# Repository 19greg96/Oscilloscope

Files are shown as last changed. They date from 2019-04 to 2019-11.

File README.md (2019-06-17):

# Oscilloscope
Simple two channel oscilloscope, function generator and bode plotter for STM32 NUCLEO-F446RE board.

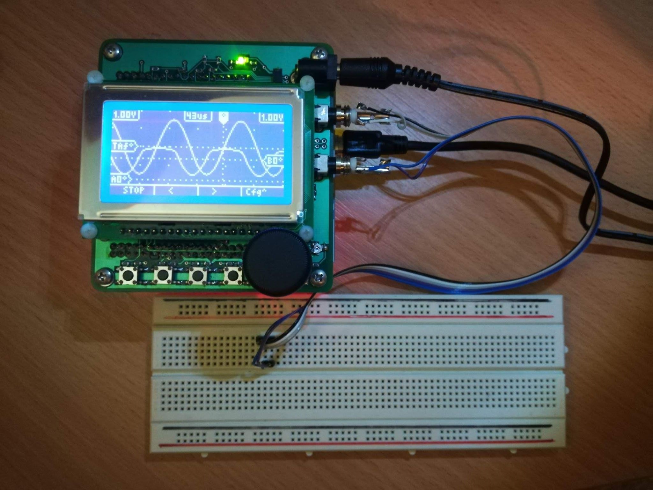
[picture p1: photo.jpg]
Picture of oscilloscope measuring effect of LED on DAC channel 2, when internal DAC buffer is disabled

Picture of oscilloscope measuring effect of LED on DAC channel 2, when internal DAC buffer is disabled.

## Issues with the hardware design:
 - Input voltage range is bad (5Vpp). This can be extended by switchable voltage divider on input.
 - No separate analog / digital ground plane.
 - Input trace has no extra clearance from ground planes.
 - GPIO pin allocation is not optimised for header side, leading to many cross board signal connections.
 - No control of anti-alias filter cut-off frequency.
 - No hardware gain control (op-amp reference should be at Vcc/2).
 - In DC coupling mode, there is a Vcc/2 offset caused by the bias for AC coupling.
 - There is an offset voltage on channel A for some reason (this could be fixed in software, but hardware explanation would be better).
 - AC coupling cutoff frequency could be lower.
 - AC coupling cutoff frequency is changed by external resistance, because there is no buffer directly on the input. (buffer needs a negative voltage rail for this)
 - DAC output single resistor is not enough for power rating. Minimum two parallel resistors are needed for 3.3V max output.
 - Max DAC output voltage is little less than Vref.
 - No support of negative DAC output.
 - Rotary encoder is too close to buttons and GLCD.
 - DC and IO jacks do not hang far enough off of PCB edge to enable boxing of device.
 - GLCD is upside-down making contrast bad at normal viewing angles.
 - No support fot 4W measurement.

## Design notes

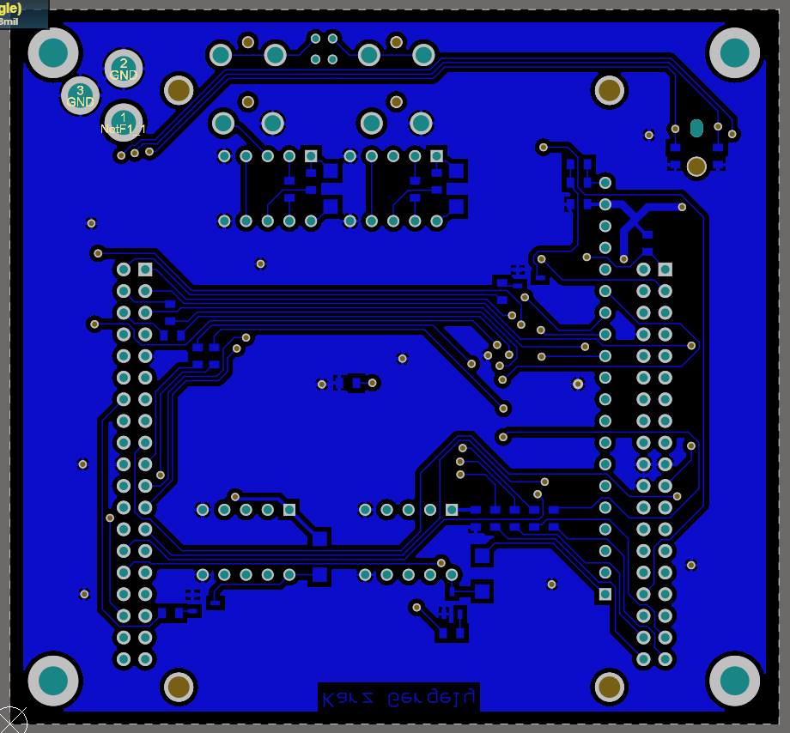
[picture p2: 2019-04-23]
oscilloscope/oscilloscope/Project Outputs for Oscilloscope/BOT_no_silk.PNG

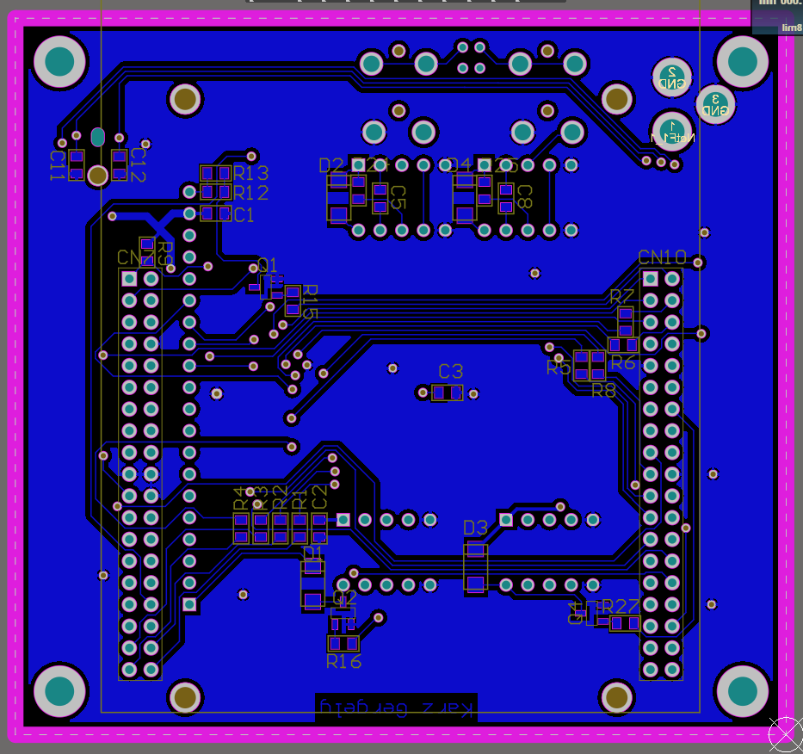
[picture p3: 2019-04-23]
oscilloscope/oscilloscope/Project Outputs for Oscilloscope/BOT_mirrored.png

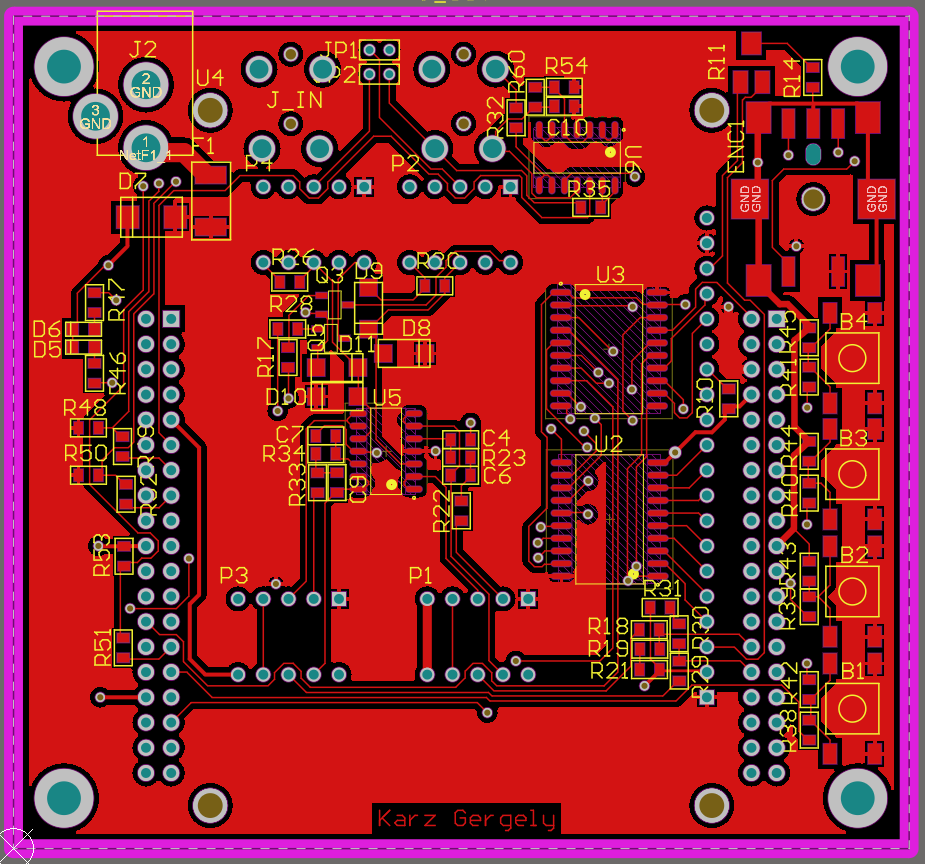
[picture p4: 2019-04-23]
oscilloscope/oscilloscope/Project Outputs for Oscilloscope/TOP.PNG

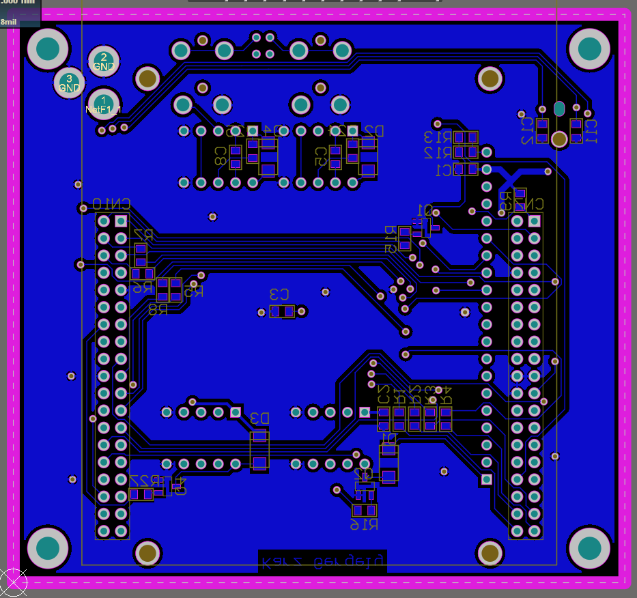
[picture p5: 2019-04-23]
oscilloscope/oscilloscope/Project Outputs for Oscilloscope/BOT.PNG

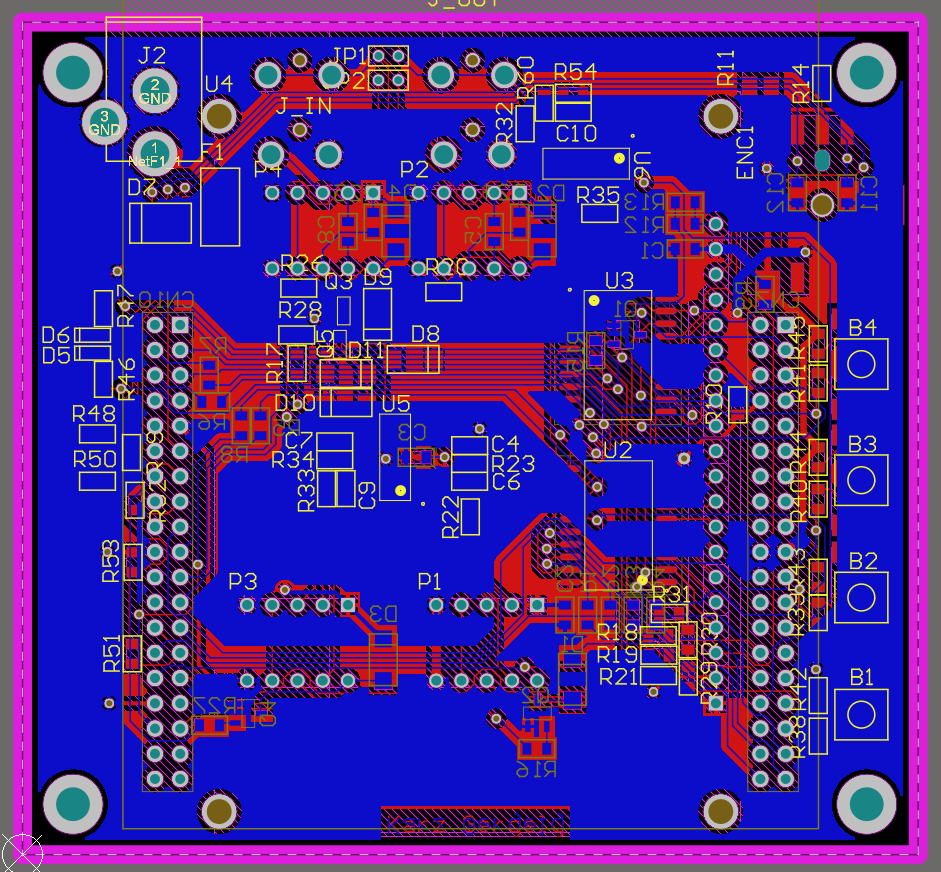
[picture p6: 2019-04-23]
oscilloscope/oscilloscope/Project Outputs for Oscilloscope/Capture.PNG

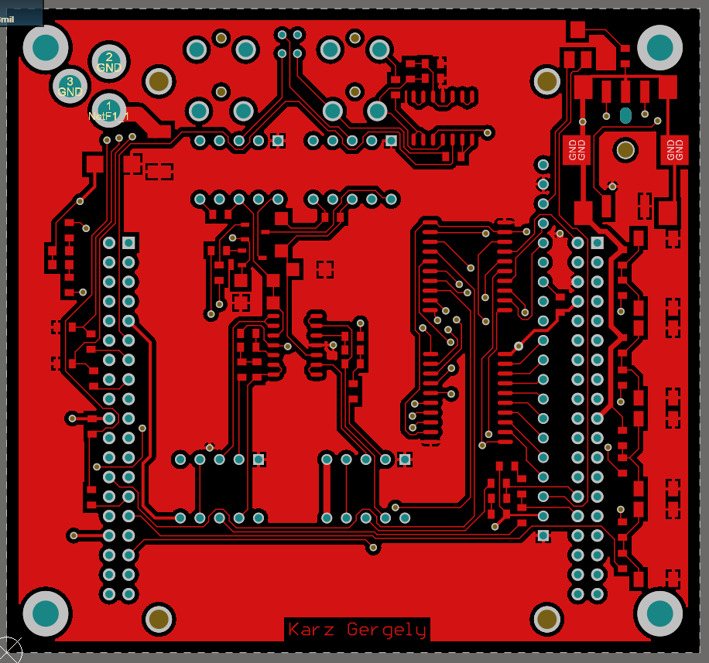
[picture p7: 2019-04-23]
oscilloscope/oscilloscope/Project Outputs for Oscilloscope/TOP_no_silk.PNG

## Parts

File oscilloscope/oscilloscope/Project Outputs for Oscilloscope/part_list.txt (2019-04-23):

Comment	Reference	Description	Designator	Footprint	LibRef	Quantity

"Button"	"45-05-42"	"Push button"	"B1, B2, B3, B4"	"FP_BTN_SMD"	"Button"	"4"
"100nF"	"82-10-76"	"Capacitor"	"C1, C2, C3, C10"	"FP_0805_CAP_085"	"CAP 100nF"	"4"
"10nF"	"82-11-02"	"Capacitor"	"C4, C5, C6, C7, C8, C9, C11, C12"	"FP_0805_CAP_085"	"CAP 10nF"	"8"
"SCHOTTKY SMA"	"83-02-20"	"Schottky diode"	"D1, D2, D3, D4, D8, D9, D10, D11"	"FP_SMA"	"SCHOTTKY SMA"	"8"
"LED Green"	"95-01-09"	"Green LED"	"D5"	"FP_0805_LED_RED"	"LED Green"	"1"
"LED Red"	"95-01-68"	"Red LED"	"D6"	"FP_0805_LED_RED"	"LED Red"	"1"
"TRANS SUPPR"	"96-03-67"	"Transient suppressor"	"D7"	"FP_SMB"	"TRANS SUPPR"	"1"
"Rotary Encoder"	""	"Encoders 9.5 MM SHAFT W/SWITCH 2 DET"	"ENC1"	"FP_PEC11S"	"PEC11S-929K"	"1"
"Multifuse"	"44-04-71"	"1812 Multifuse"	"F1"	"FP_MULTIFUSE"	"Multifuse"	"1"
"2.xmm"	"43-07-67"	"2.xmm DC HEBA25 TÁPFESZÜLTSÉG ALJZAT ZÁRT, NYÁKBA 90°"	"J2"	"FP_DC_TAP_ANYA"	"DC_TAP_ANYA"	"1"
"35mm Audio Jack 3 contact"	"1267376"	"3.5mm Audio Jack MX-387GL"	"J_IN, J_OUT"	"FP_35MM_JACK_SMALL_3PIN"	"35mm Audio Jack 3 contact"	"2"
"JUMPER"	""	"Jumper Wire"	"JP1, JP2"	"FP_CONN2_TUSKE_2MM_1.5+3.2"	"JUMPER"	"2"
"Relay"	"42-17-08"	"Mini DPDT relay 14x9x5mm"	"P1, P2, P3, P4"	"FP_RELAY"	"Relay Mini DPDT"	"4"
"2N7002"	"86-05-52"	"N-channel MOSFET"	"Q1, Q2, Q3, Q4, Q5"	"FP_SOT23-3"	"2N7002"	"5"
"1K"	"81-27-93"	"Resistor"	"R1, R2, R3, R4, R5, R6, R7, R8, R18, R19, R21, R29, R30, R31, R38, R39, R40, R41, R51"	"FP_0805_RES"	"RES 1K"	"19"
"100K"	"81-30-68"	"Resistor"	"R9"	"FP_0805_RES"	"RES 100K"	"1"
"10K"	"81-30-45"	"Resistor"	"R10, R15, R16, R17, R27, R28, R42, R43, R44, R45, R48, R49, R50, R52, R53, R54, R60"	"FP_0805_RES"	"RES 10K"	"17"
"4K7"	"90-00-68"	"4K70 3305-472R (KIC) 3x3.8mm CERMET"	"R11"	"FP_CERMET_SMD"	"Cermet Pot 4K7"	"1"
"100R"	"81-30-00"	"Resistor"	"R12, R13"	"FP_0805_RES"	"RES 100R"	"2"
"6K8"	"81-30-41"	"Resistor"	"R14"	"FP_0805_RES"	"RES 6K8"	"1"
"2M00"	"80-17-98"	"Resistor"	"R20, R24, R25, R26"	"FP_0805_RES"	"RES 2M"	"4"
"820R"	"81-30-21"	"Resistor"	"R22, R23, R33, R34"	"FP_0805_RES"	"RES 820R"	"4"
"150R"	"81-10-77"	"Resistor"	"R32, R35, R46, R47"	"FP_0805_RES"	"RES 150R"	"4"
"NUCLEO-F446RE"	"NUCLEO"	""	"U1"	"FP_NUCLEO-64"	"NUCLEO-F446RE"	"1"
"74HCT245"	"87-06-35"	"8x Bidirectional bus transciever"	"U2"	"FP_SOP127P1030X265-20M"	"74HCT245"	"1"
"74HCT244D"	"87-05-95"	"8xBuffer/Line Driver"	"U3"	"FP_SOP127P1030X265-20M"	"74HCT244D"	"1"
"GLCD_64128Q"	"37-00-71"	"64128QCCBW-3LP"	"U4"	"FP_GLCD_64128Q"	"GLCD_64128Q"	"1"
"MCP6004T-I/SL"	"1627186"	"Operational Amplifier, Quad, 4 Amplifier, 1 MHz, 0.6 V/µs, 1.8V to 5.5V, SOIC, 14 Pins"	"U5, U6"	"FP_SOIC127P600X175-14M"	"MCP6004T-I/SL"	"2"

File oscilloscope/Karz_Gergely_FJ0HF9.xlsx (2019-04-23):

Item # | Supplier | Reference | Name | Quantity
1 | Farnell | 1267376 | MX-387GL - Phone Audio Connector, 3 Contacts, Jack, 3.5 mm, PCB Mount, Metal Body | 2
2 | Farnell | 1627186 | MCP6004T-I/SL - Operational Amplifier | 2
3 | Lomex | 43-07-67 | TÁP DC ANYA 5.5/2.1/9.5mm DCS-5521-5 | 1
4 | Lomex | 90-00-68 | 4K70 3305-472R (KIC) 3x3.8mm CERMET | 1
5 | Lomex | 87-06-35 | 74HCT245D Transceiver, 74HCT245 | 1
6 | Lomex | 87-05-95 | 74HCT244D-Q100,118 Buffer / Line Driver, 74HCT244 | 1
7 | Lomex | 44-04-71 | 1.25A 15V 1812L125/16DR POLYFUSE SMD 1812 (LFS) ˝LF125-16˝ | 1
8 | Lomex | 37-00-71 | 128x 64 DOT LIGHT:LED 64128QCCBW-3LP (DIS) 0.4/DOT 75x53mm BLUE STN LOW.POW. WIDE TEMP. (CONTROLLER/DRIVER: SBN6400G-D + SBN0064G-D) | 1
9 | Lomex | 82-10-76 | 100nF 0805 10% 50V X7R 0805B104K500CT (WAL) | 4
10 | Lomex | 82-11-02 | 10nF 0805 10% 100V X7R 08051C103KAT2A (AVX) | 8
11 | Lomex | 95-01-09 | 2012 GREEN 568nm 15mcd KP-2012SGC (KIN) W.CLEAR 2x1.2x1.1mm 0805 120° | 1
12 | Lomex | 42-17-08 | MECH 5V 2xMORSE 1A/30VDC 0.5A/12VAC A5W-K (TAK) 178R 14x9x5mm | 4
13 | Lomex | 86-05-52 | MOSFET Transistor, N Channel, 300mA, 60V, 2.8 ohm, 10V, 2V | 5
14 | Lomex | 45-05-42 | TACT 6x 6 4P SPST 1 FSM2JSMA (TYC) 50mA 12VDC SMD H=4.3mm 160g BLACK B. 2-1437565-7 | 4
15 | Lomex | 95-01-68 | 2012 RED 640nm 100mcd KP-2012SRC-PRV (KIN) W.CLEAR 2x1.2x1.1mm 0805 120° | 1
16 | Lomex | 81-27-93 | 1K00 0805 5% WR08X102JTL 0.125W (WAL) | 19
17 | Lomex | 81-30-68 | 100K 0805 5% WR08X104JTL 0.125W (WAL) | 1
18 | Lomex | 81-30-45 | 10K0 0805 5% CR-05JL7---10K 0.125W (VIK) | 17
19 | Lomex | 81-30-00 | 100R 0805 5% WR08X101JTL 0.125W (WAL) | 2
20 | Lomex | 81-30-41 | 6K80 0805 5% WR08X682JTL 0.125W (WAL) | 1
21 | Lomex | 80-17-98 | 2M00 0805 1% CR-05FL7---2M0 0.125W (VIK) | 4
22 | Lomex | 81-30-21 | 820R 0805 5% WR08X821JTL 0.125W (WAL) | 4
23 | Lomex | 81-10-77 | 150R 0805 5% CR-05JL7--150R 0.125W (VIK) | 4
24 | Lomex | 83-02-20 | 1A 40V DO-214AC SCH.RECT.LOW Vf SSL14 (TSC) SMA | 8
25 | Lomex | 96-03-67 | 6.7V Ubr 600W UNIDIR. 5V Urwm SMBJ5.0A (STM) DO-214AA (SMB) ˝BUZ˝ | 1
26 | Tanszék | NUCLEO | Nucleo F446RE | 1
27 | Lomex | 24-01-70 | ADAPTER 2000mA 5VDC KAPCSOLÓ ÜZEM 5V 2A SA110R-05GS-I (SAC) TÜV/CE 5.5/2.1mm DUGÓ EFF.LEVEL VI STANDBY POWER <0,075W | 1
28 | Lomex | 43-08-37 | TÜSKESOR 40 P PHSS-40-12/3 (T-T) 2.54mm PIN 0.64x0.64 TÖRDELHETÖ | 1
29 | Lomex | 43-00-08 | HÜVELY 20 P FHSH-2.54-20 (T-T) 1# h=8,5mm AU. | 1
30 | Lomex | 43-07-86 | JUMPER 2 P ANYA MJF-6MM (T-T) 1# FEKETE FÜLES | 2
31 | Lomex | 43-18-67 | JACK 3.5mm APA JM35STPATB (T-T) SZTEREO A-V | 2
32 | Lomex | 43-08-40 | BNC 1 P ANYA BNC-S12 (FEM) H-F SORKAPOCS BEKÖTÉSŰ LENGŐ | 4
33 | Lomex | 54-00-25 | ARNY.KÁBEL 2x0.08 AK-2-0.08F ( ) BLACK 2xD=2.8mm FLAT | 1

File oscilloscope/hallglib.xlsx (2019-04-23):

Item # | Column=Supplier | Column=Reference | Column=Name | Column=Quantity
1
2
3

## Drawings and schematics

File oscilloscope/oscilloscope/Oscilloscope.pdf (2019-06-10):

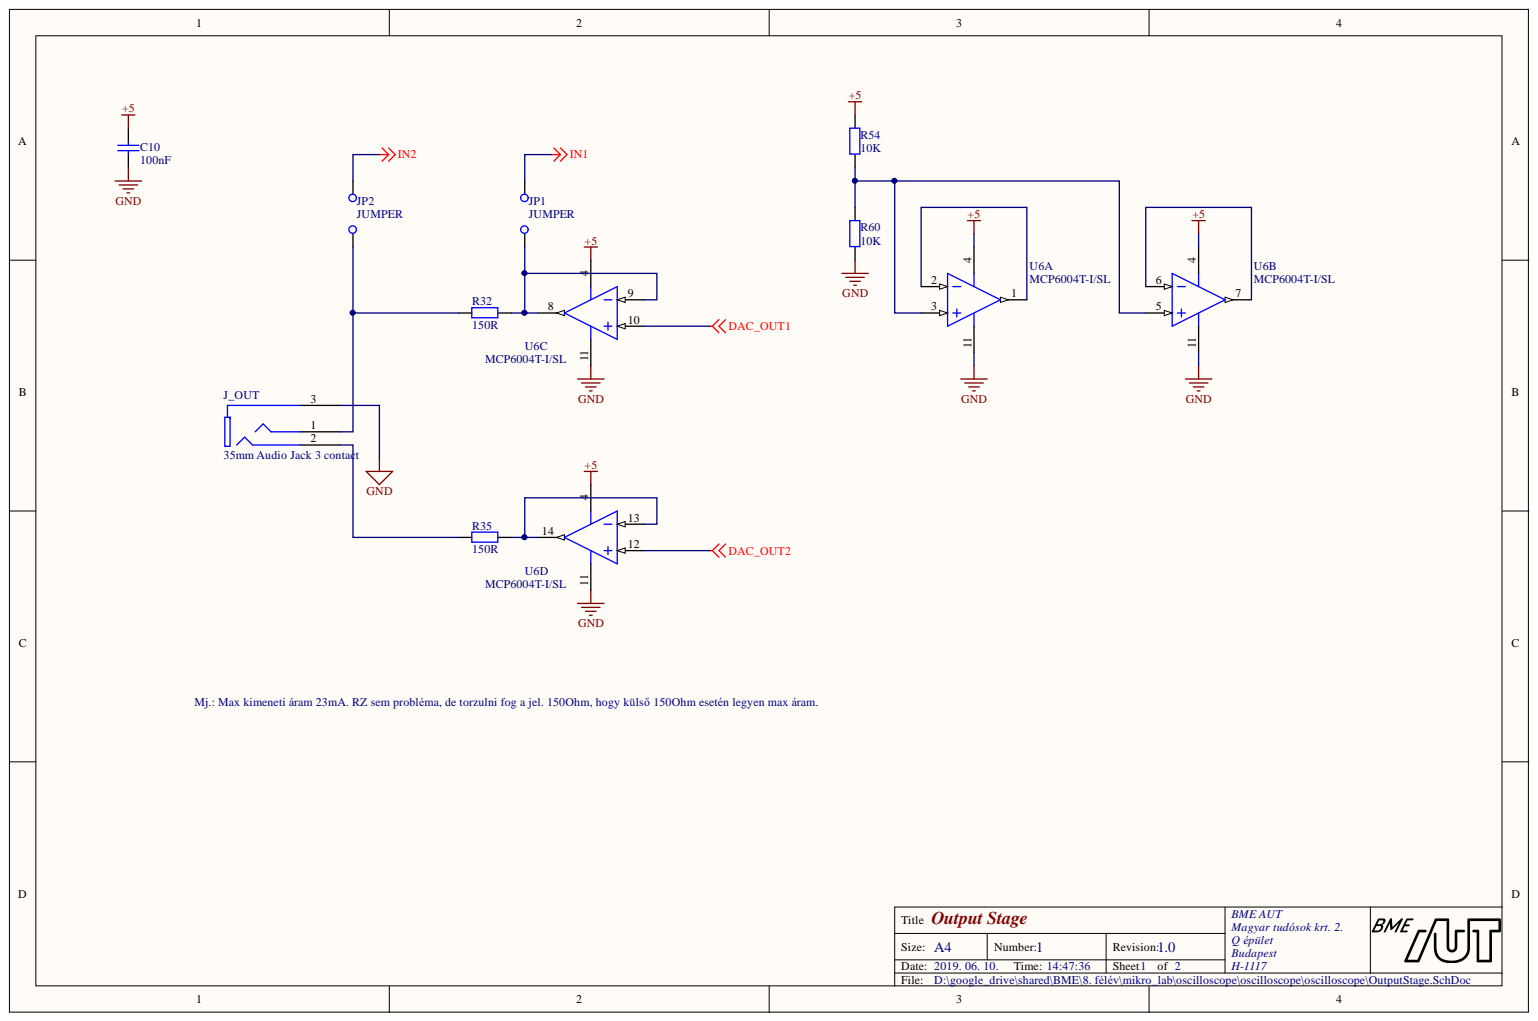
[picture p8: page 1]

Mj.: Max kimeneti áram 23mA. RZ sem probléma, de torzulni fog a jel. 150Ohm, hogy külső 150Ohm esetén legyen max áram.

Output Stage Title | BME AUT Magyar tudósok krt. 2. Q épület Budapest H-1117

A4 Size: | 1 Number: | 1.0 Revision:
Date: 2019. 06. 10. Time: 14:47:36 | | Sheet of 2

D:\google_drive\shared\BME\8. félév\mikro_lab\oscilloscope\oscilloscope\oscilloscope\OutputStage.SchDoc

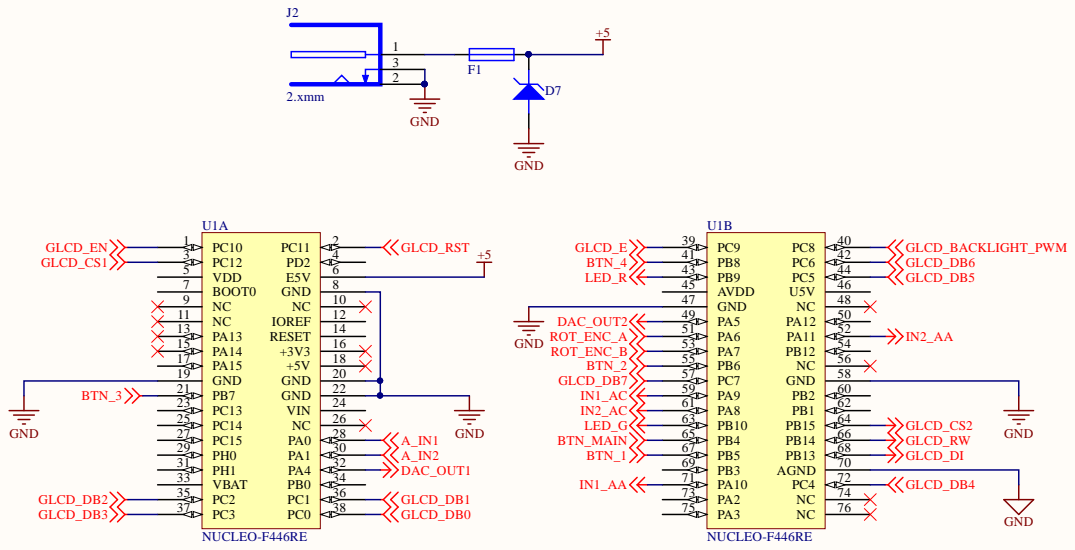
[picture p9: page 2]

Nucleo Title | BME AUT Magyar tudósok krt. 2. Q épület Budapest

A4 Size: | 1 Number: | 1.0 Revision:

D:\google_drive\shared\BME\8. félév\mikro_lab\oscilloscope\oscilloscope\oscilloscope\Nucleo.SchDoc

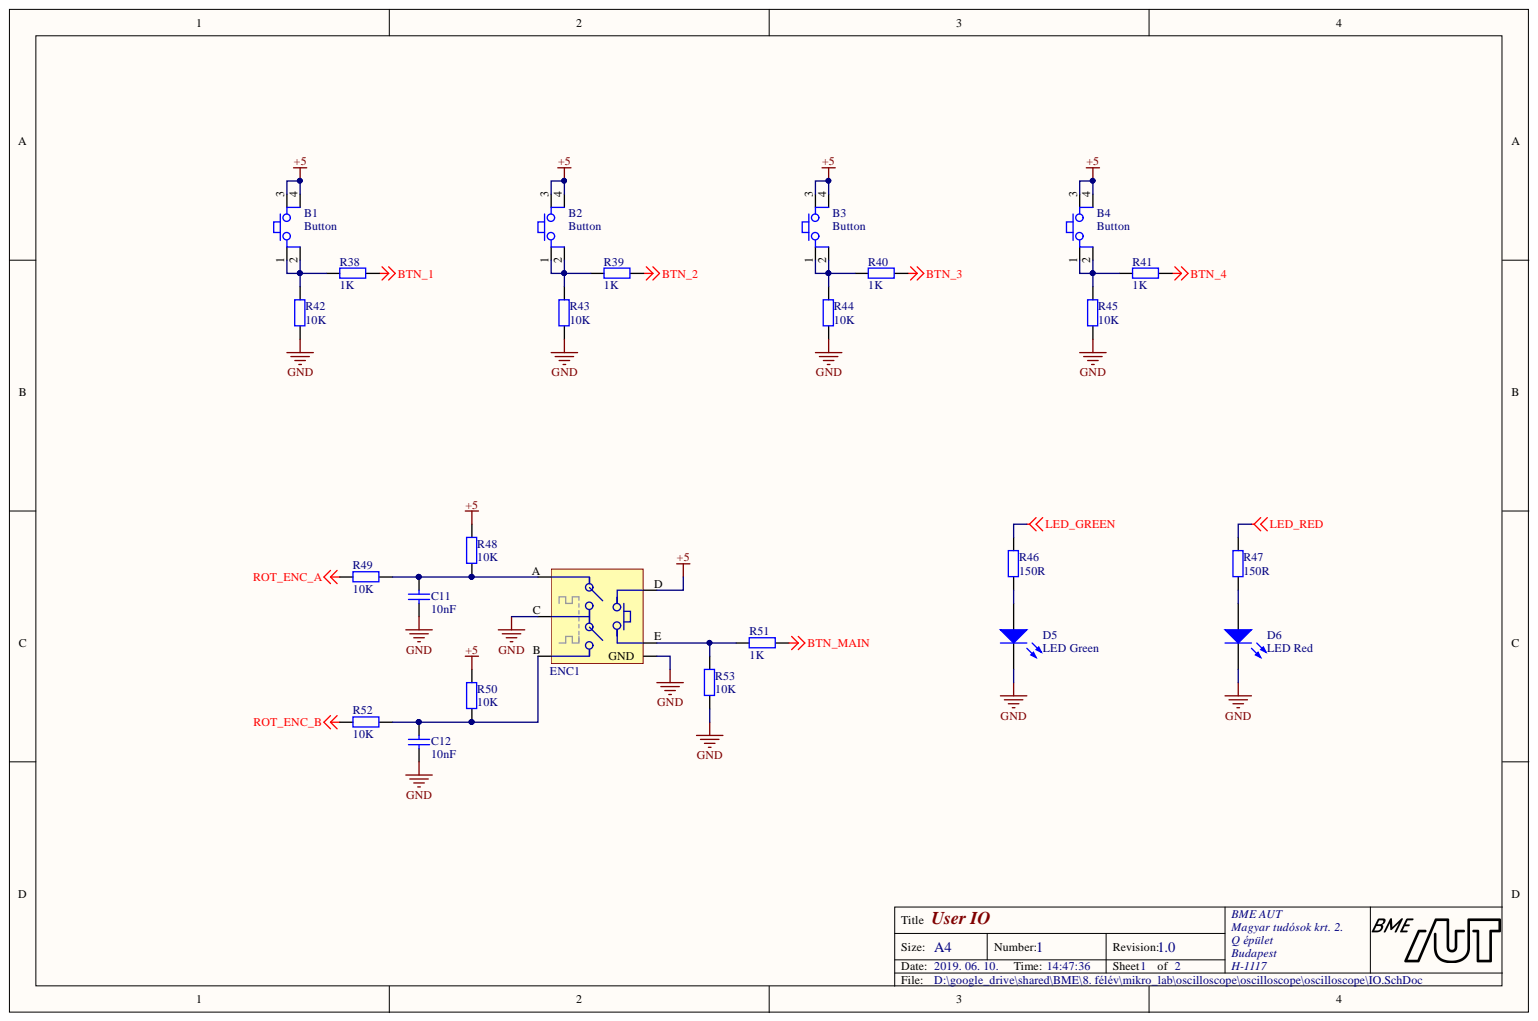
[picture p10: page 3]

User IO Title | BME AUT Magyar tudósok krt. 2. Q épület Budapest

A4 Size: | 1 Number: | 1.0 Revision:

D:\google_drive\shared\BME\8. félév\mikro_lab\oscilloscope\oscilloscope\oscilloscope\IO.SchDoc

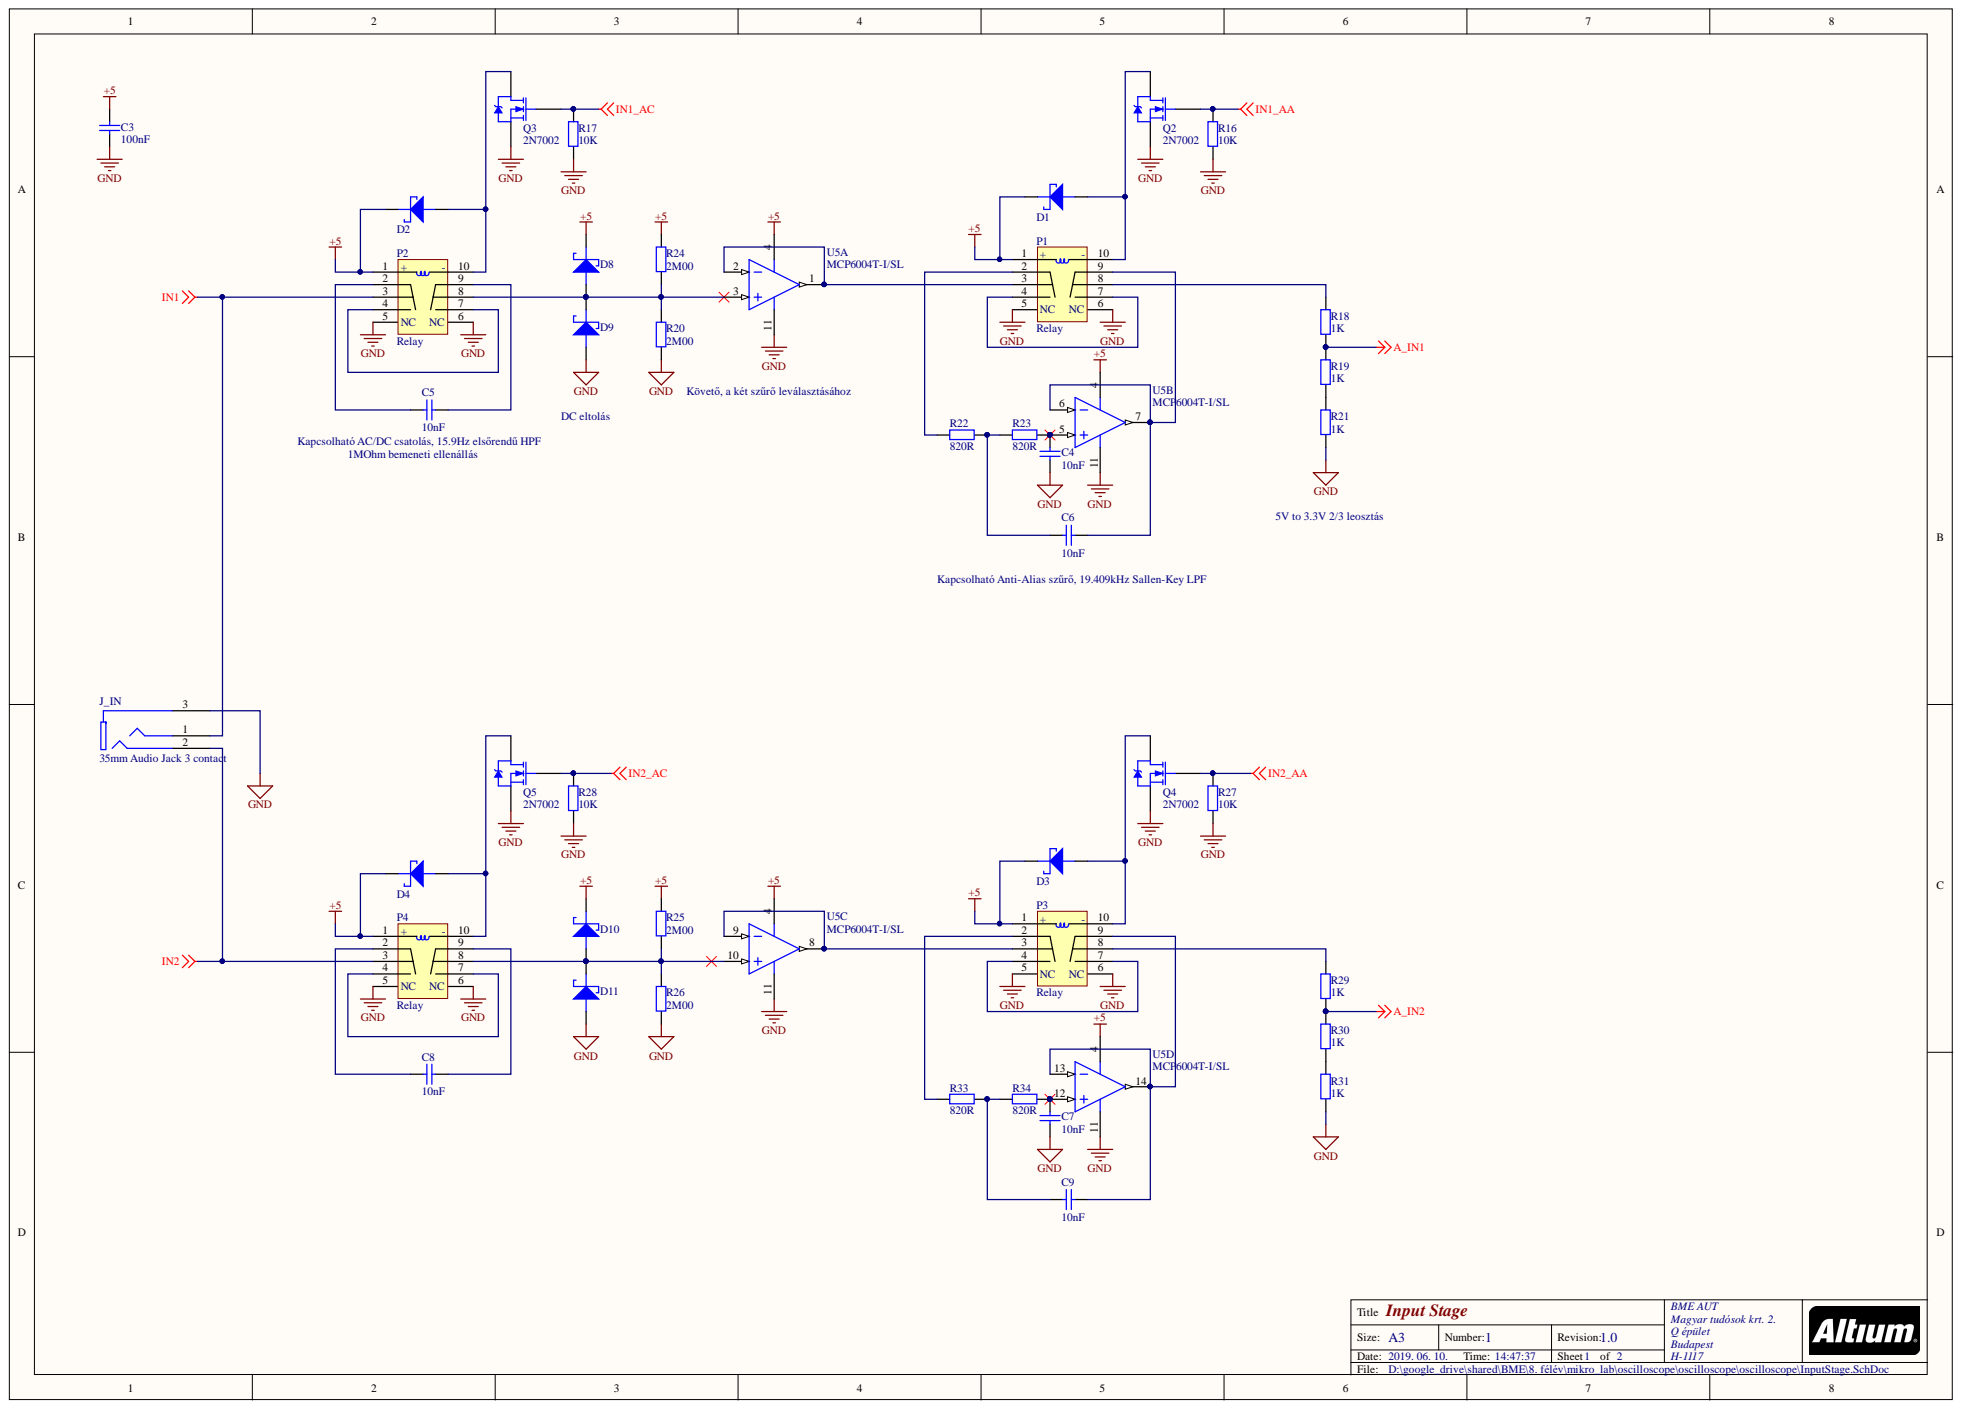
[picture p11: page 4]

Inpu t S tage Ti t l e | BME A UT Magyar tud ó sok kr t. 2. Q ép ü let Budapes t H-

Size: A | Number : 1 | Revi s ion: 1.0

Ti me: | | Sheet of

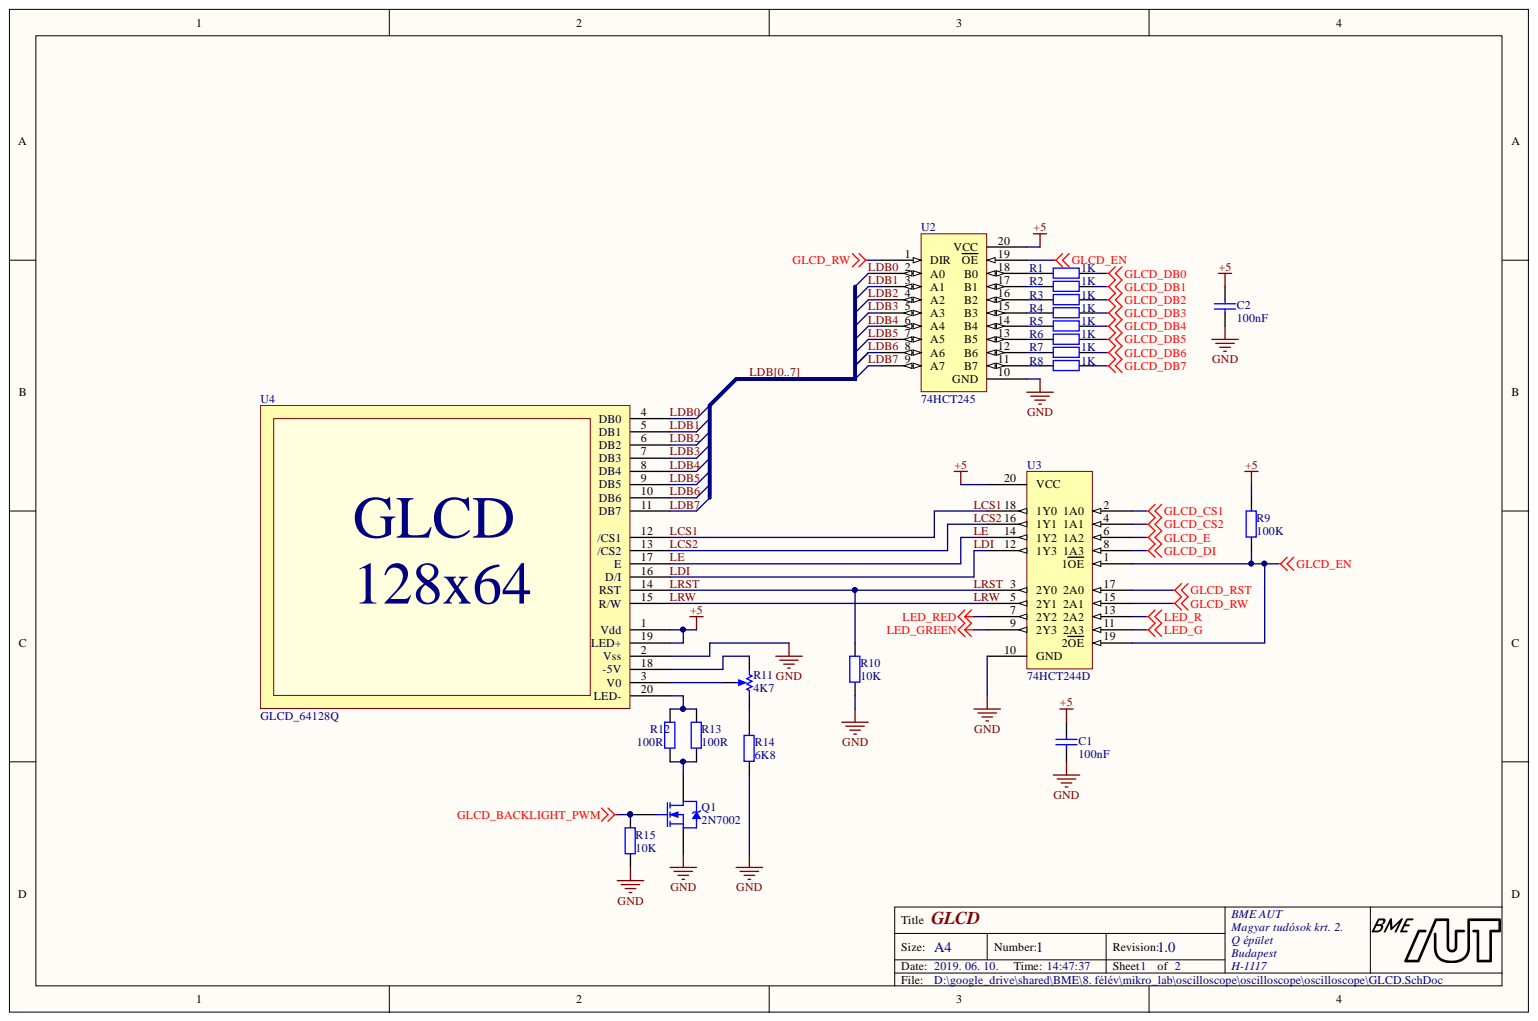
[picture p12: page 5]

+5 GND 12 B5 13 B4 14 B3 15 B2 16 B1 17 B0 18 OE 19 1 B6 R3 | 1 K

R5 | 1 K
R6 | 1 K

LCS1 LCS2 LDI LRST LRW LE | 1 4 | 6

1 3 | | 1 2 | 8
1 7 | | 3
1 6

+5 | L E D _RE D L E D _ GRE E N | 7

GLCD T i t l e | B ME A U T Ma gya r t u d ó s ok kr t. 2 . Q ép ü let B u d apes t H-1

A4 Size: | 1 N umber: | 1.0 Rev i s i o n :

9. 0 6. 1 . T ime: : : | | Sheet o f

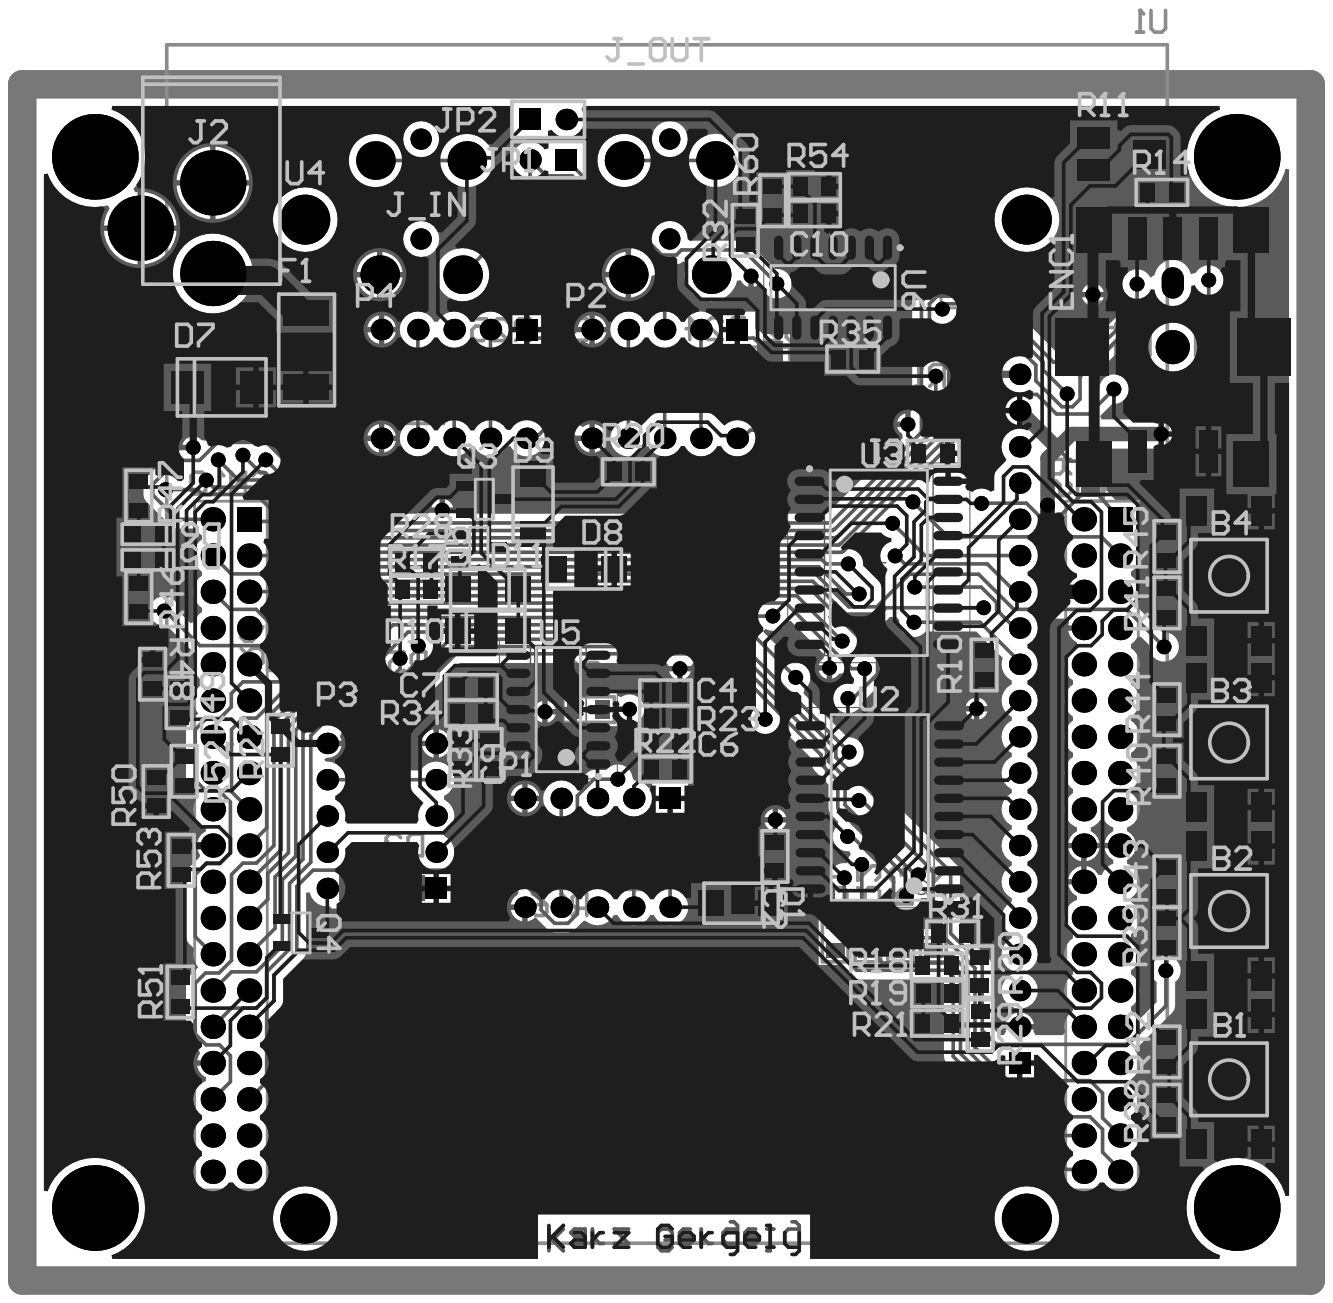
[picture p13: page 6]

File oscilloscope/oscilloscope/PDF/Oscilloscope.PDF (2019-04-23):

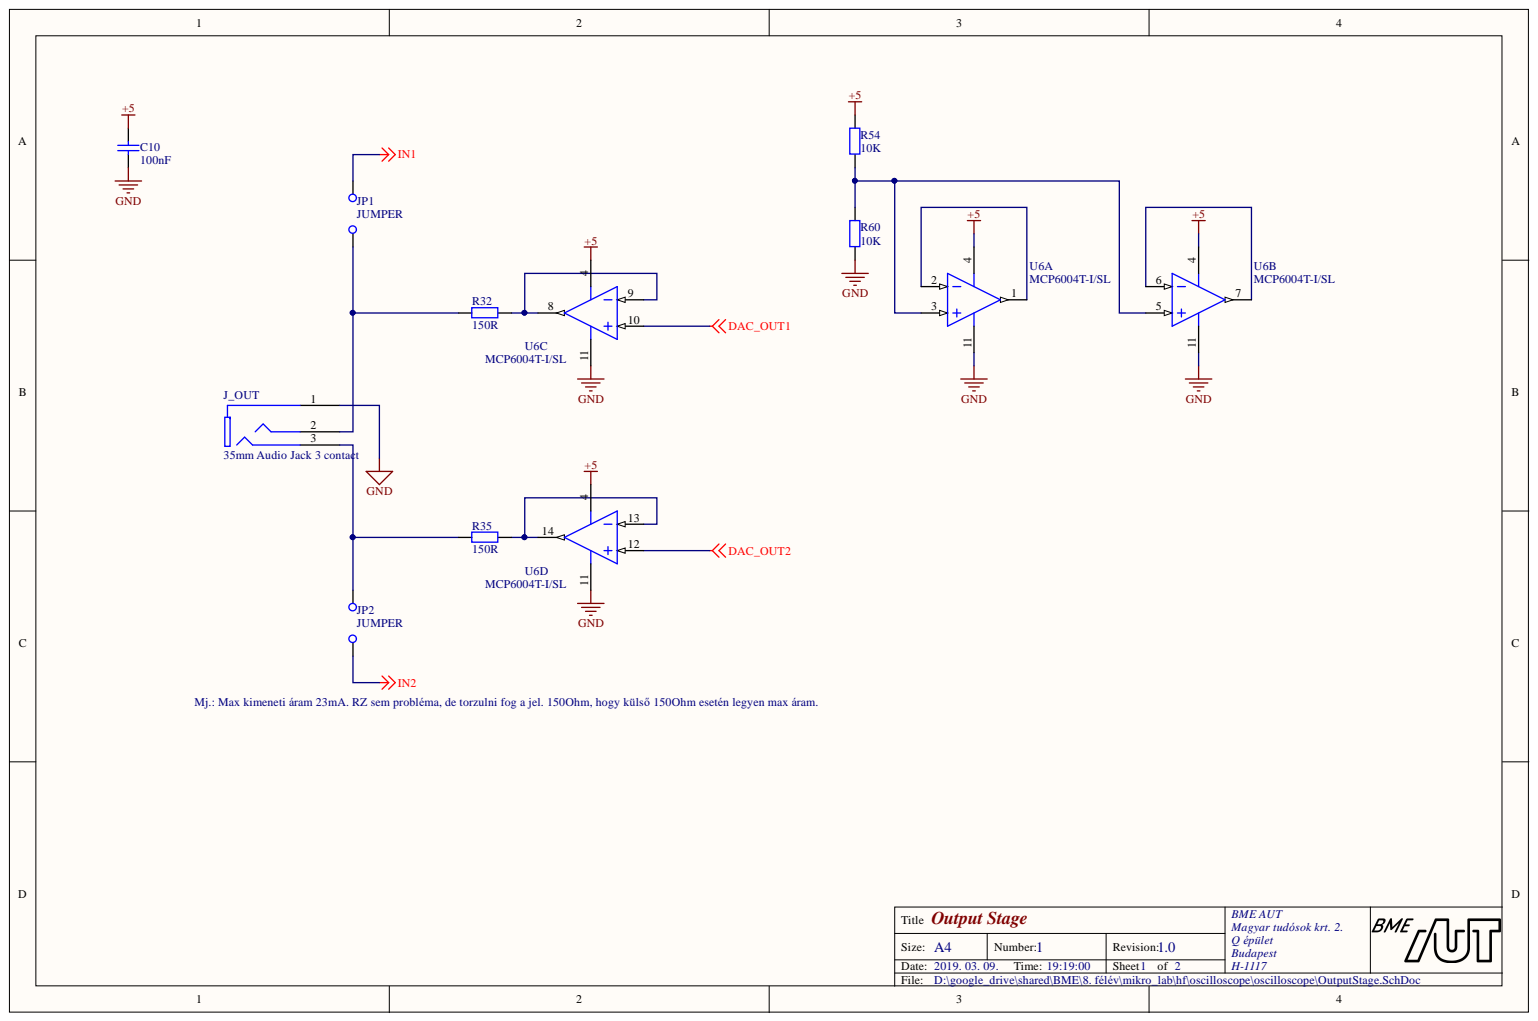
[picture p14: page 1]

Output Stag e T i t l e | B ME A U T Ma gya r t u d ó s ok kr t. 2 . Q ép ü let B u d apes t H-1

A4 Size: | 1 N umber: | 1.0 Rev i s i o n :
Date: 9. 0 3. 0 . T ime: : | | Sheet o f

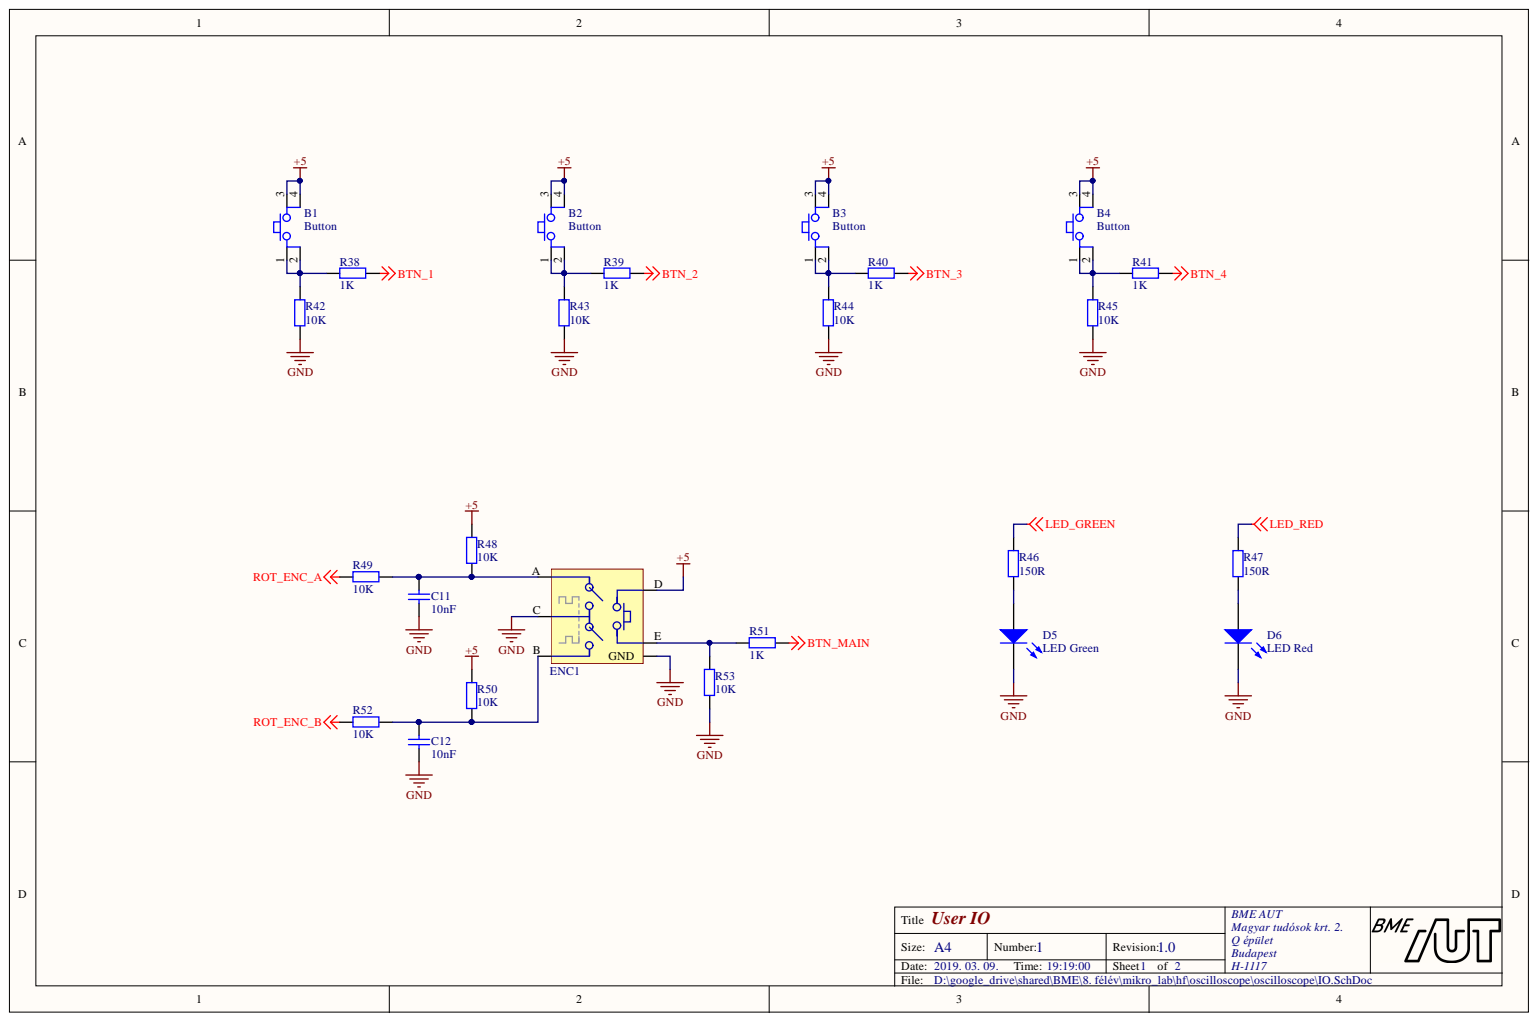
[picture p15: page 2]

User IO Title | BME AUT Magyar tudósok krt. 2. Q épület Budapest H-1117

A4 Size: | 1 Number: | 1.0 Revision:
2019. 03. 09. Time: 19:19:00 | | Sheet of 2

D:\google_drive\shared\BME\8. félév\mikro_lab\hf\oscilloscope\oscilloscope\IO.SchDoc

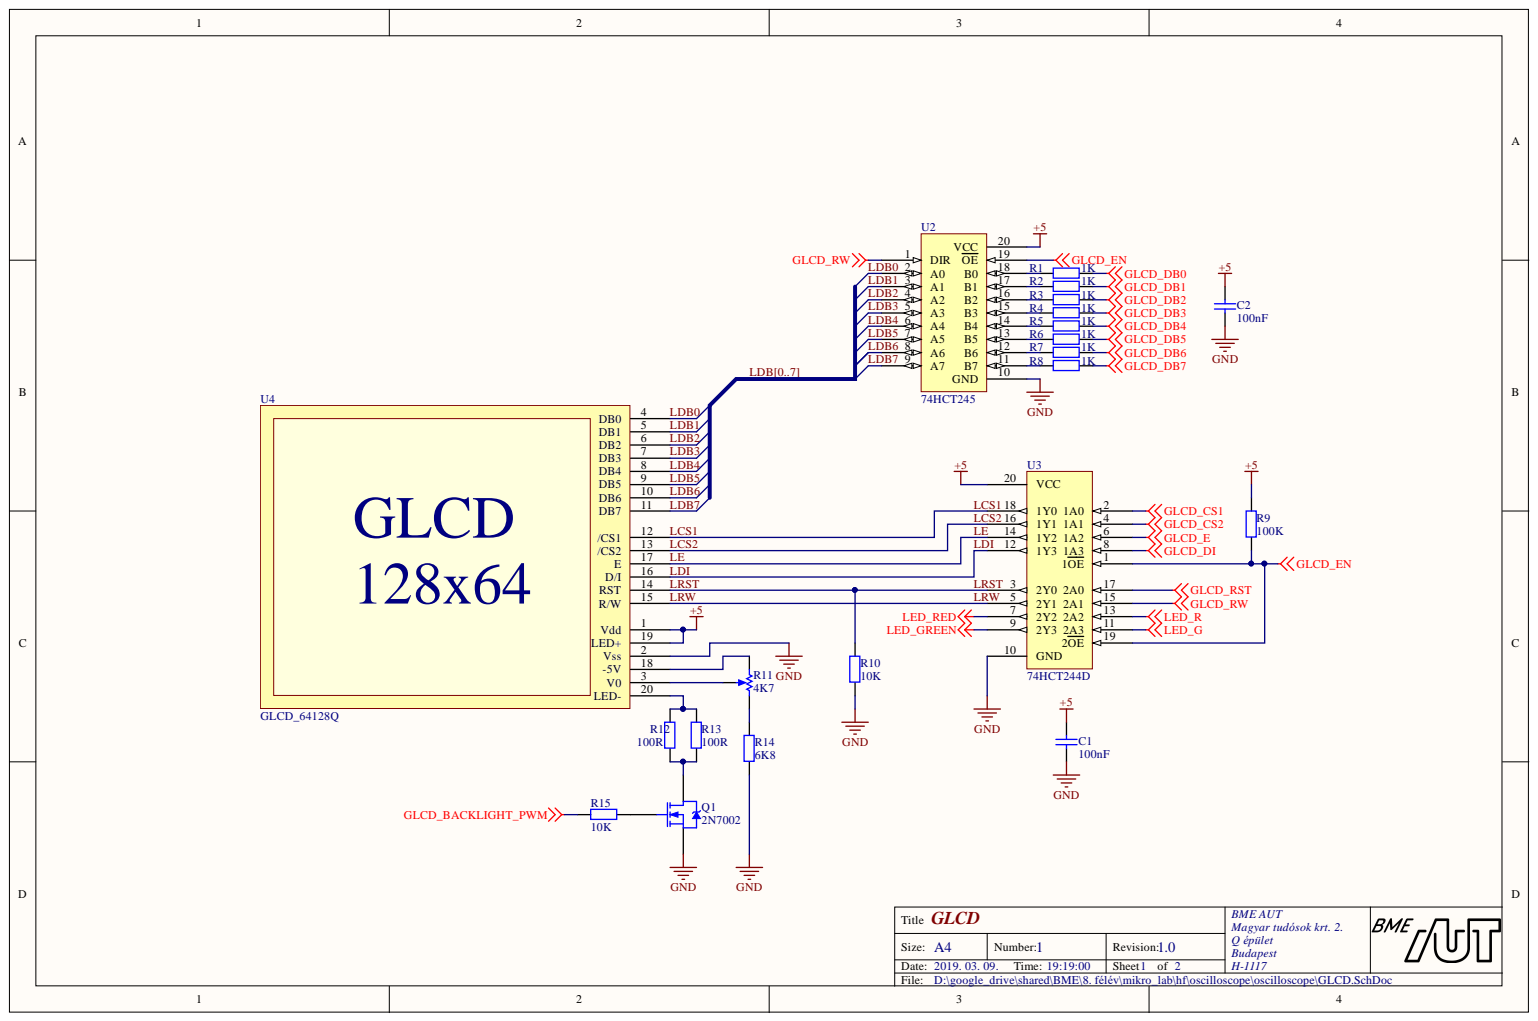
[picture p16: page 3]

+5 GND 12 B5 13 B4 14 B3 15 B2 16 B1 17 B0 18 OE 19 1 B6 R3 | 1 K

R5 | 1 K
R6 | 1 K

LCS1 LCS2 LDI LRST LRW LE | 1 4 | 6

1 3 | | 1 2 | 8
1 7 | | 3
1 6

+5 | L E D _RE D L E D _ GRE E N | 7

GLCD T i t l e | B ME A U T Ma gya r t u d ó s ok kr t. 2 . Q ép ü let B u d apes t H-1

A4 Size: | 1 N umber: | 1.0 Rev i s i o n :

9. 0 3. 0 . T ime: | | Sheet o f

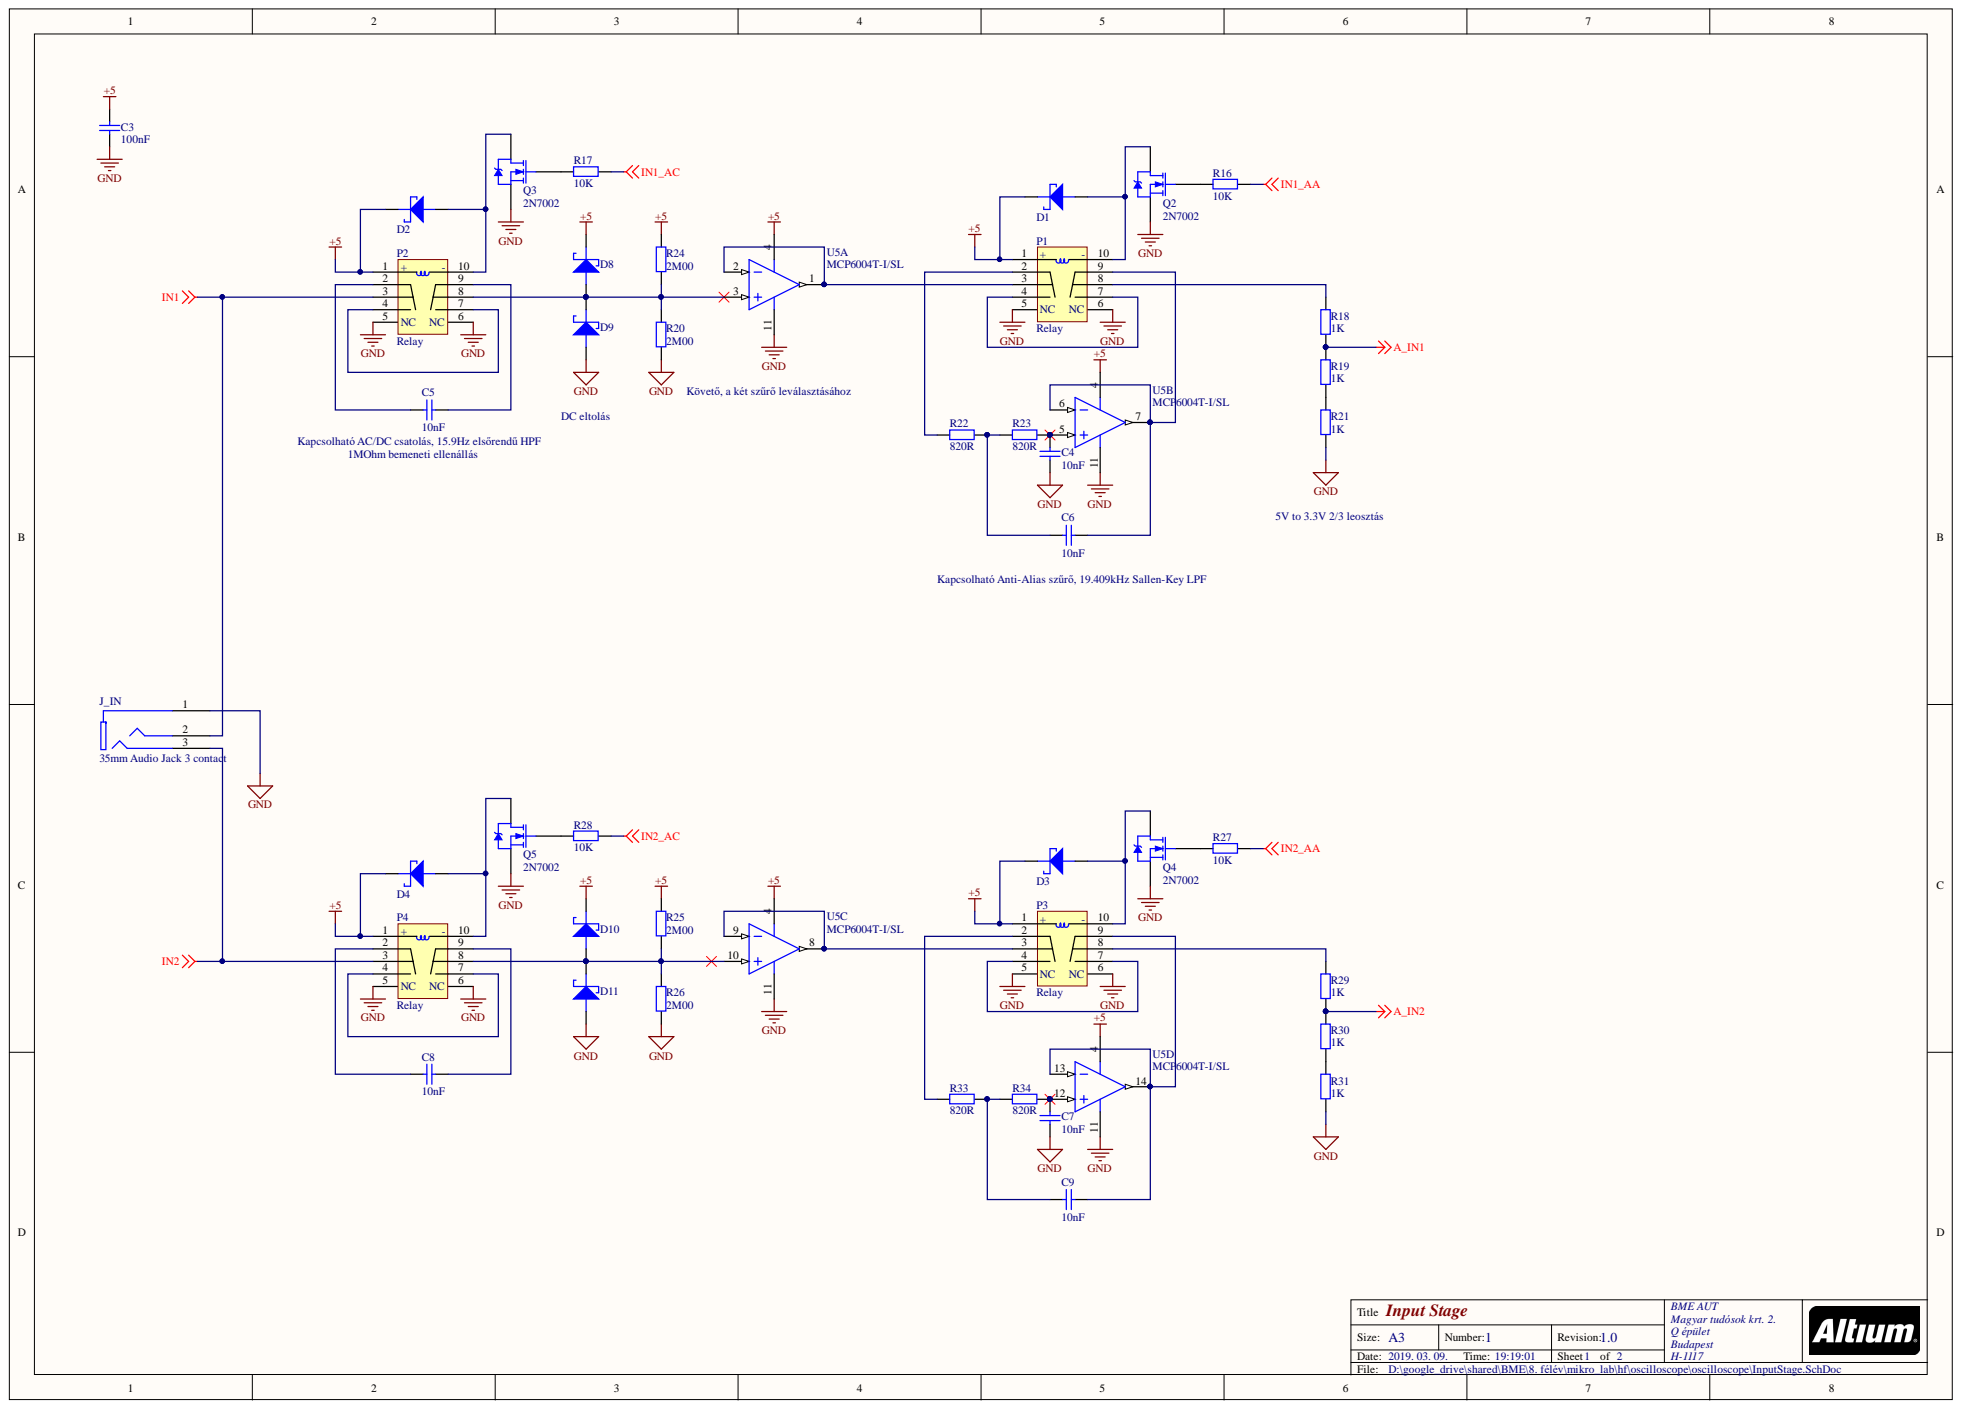
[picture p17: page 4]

Inpu t S tage Ti t e | BME A UT Magyar tud ó sok kr t. 2. Q ép ü let Budapes t H-

Size: A | Number 1 | Revi ion: 1.0

Ti me: | | Sheet of

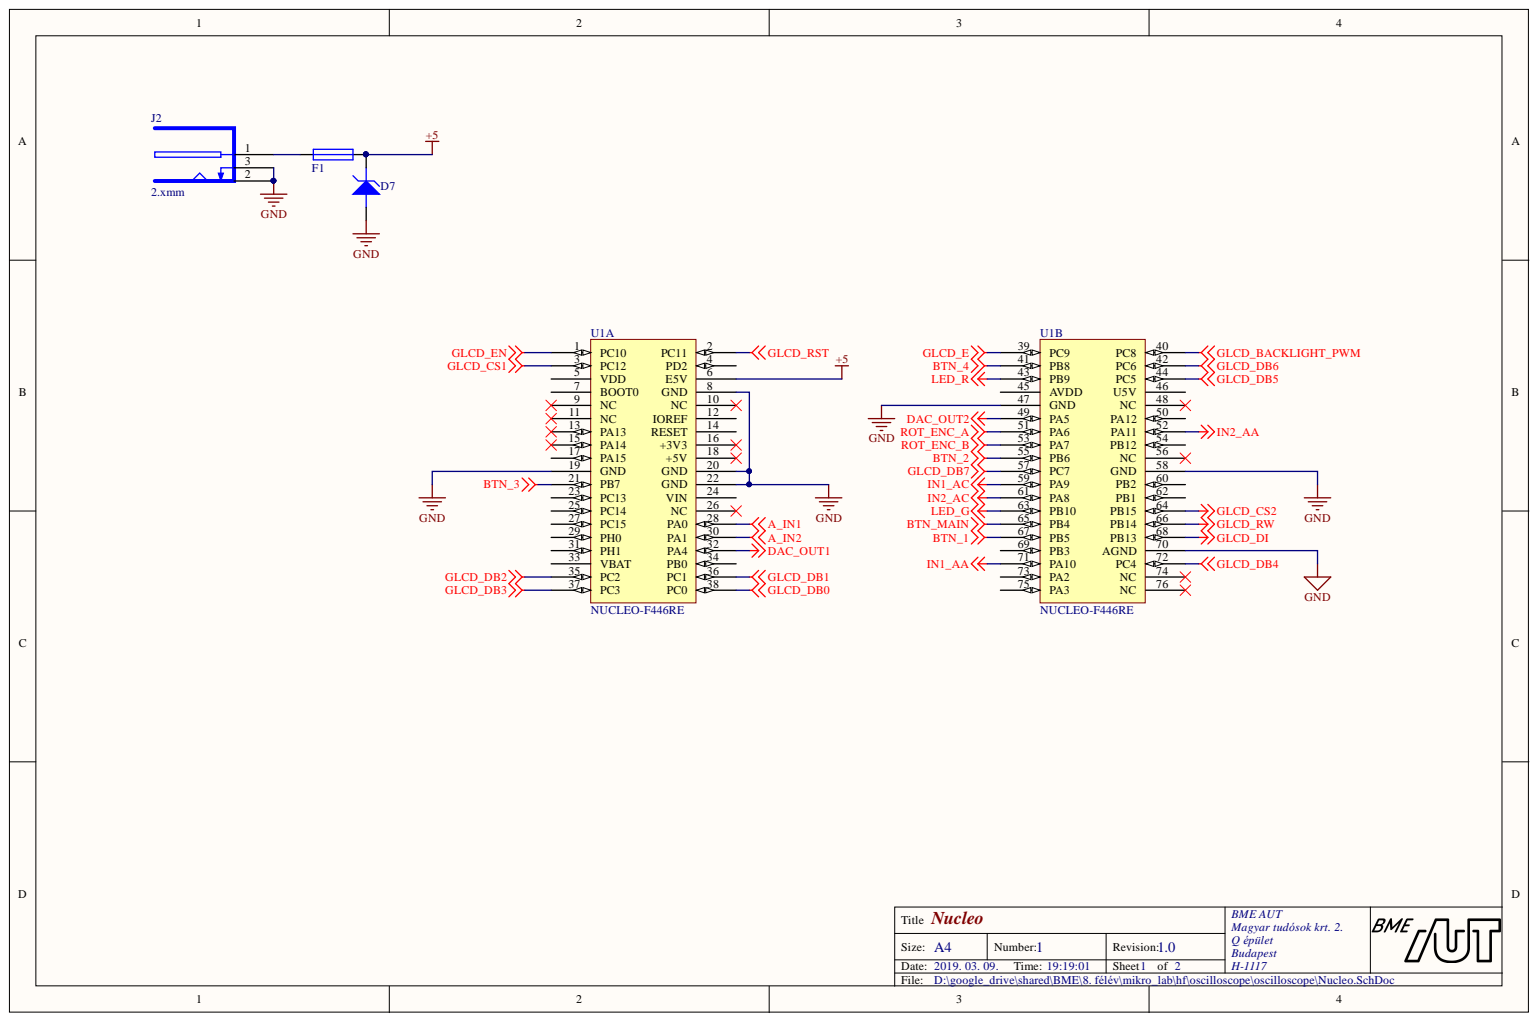
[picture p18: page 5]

Nucleo Title | BME AUT Magyar tudósok krt. 2. Q épület Budapest H-1117

A4 Size: | 1 Number: | 1.0 Revision:
2019. 03. 09. Time: 19:19:01 | | Sheet of 2

D:\google_drive\shared\BME\8. félév\mikro_lab\hf\oscilloscope\oscilloscope\Nucleo.SchDoc

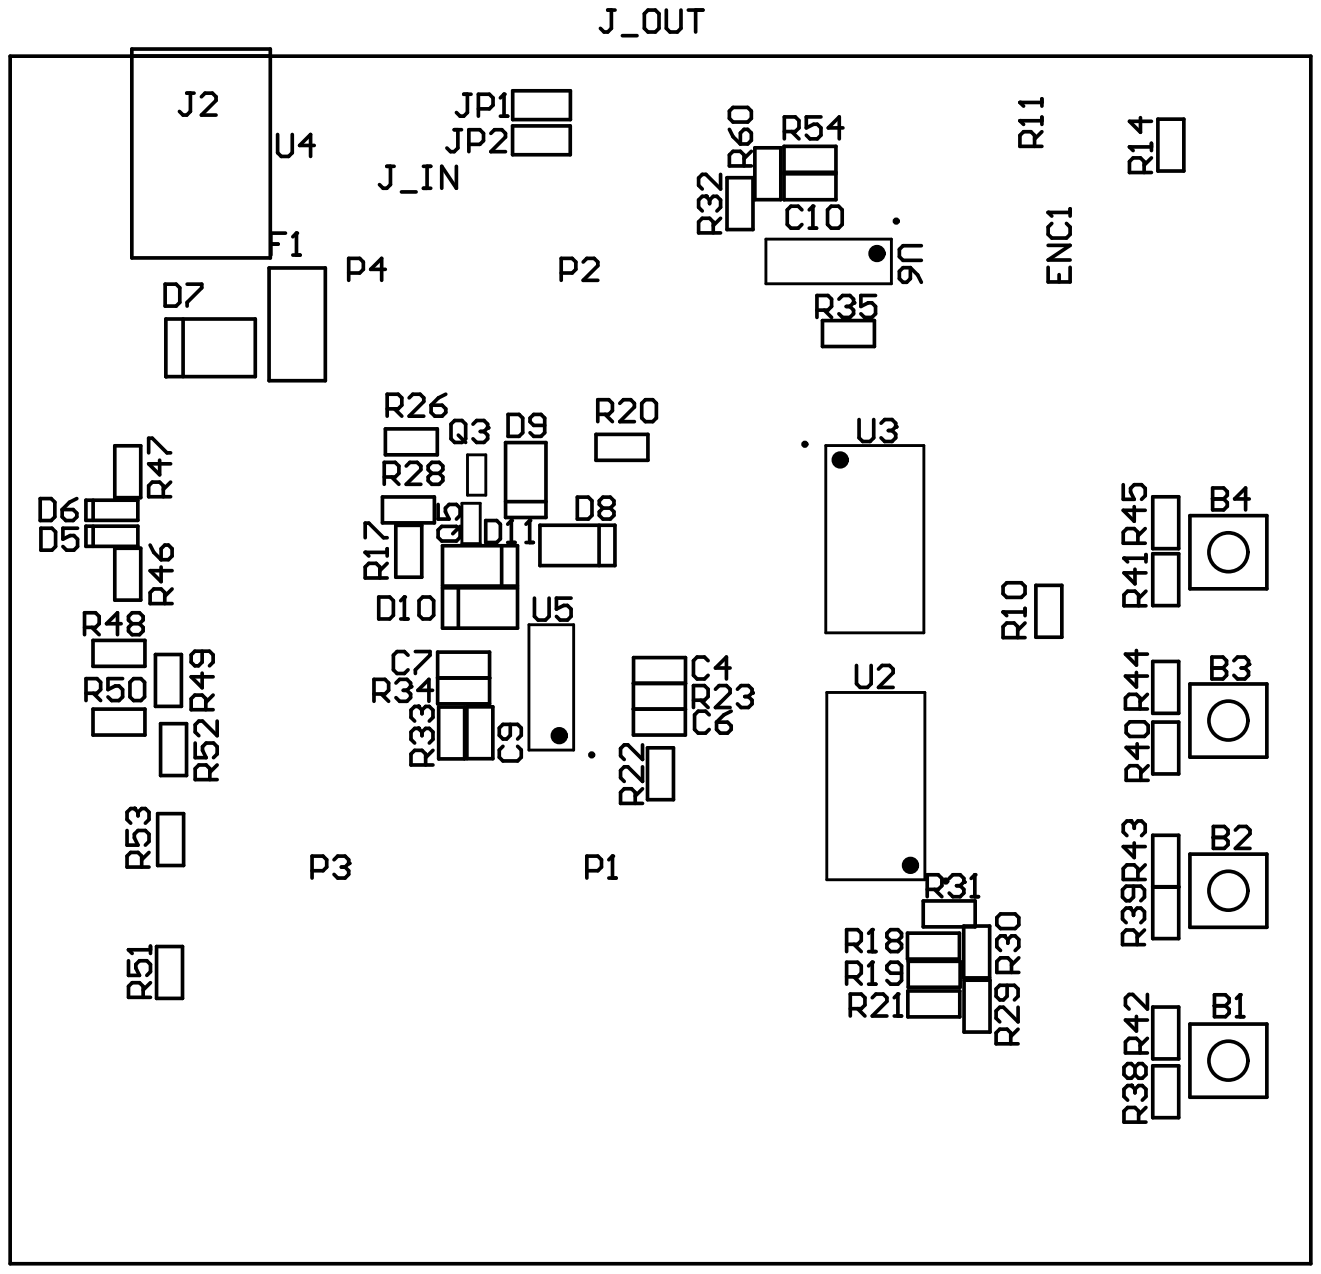
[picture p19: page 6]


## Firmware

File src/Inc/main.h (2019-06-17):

/* USER CODE BEGIN Header */
/**
  ******************************************************************************
  * @file           : main.h
  * @brief          : Header for main.c file.
  *                   This file contains the common defines of the application.
  ******************************************************************************
  ** This notice applies to any and all portions of this file
  * that are not between comment pairs USER CODE BEGIN and
  * USER CODE END. Other portions of this file, whether 
  * inserted by the user or by software development tools
  * are owned by their respective copyright owners.
  *
  * COPYRIGHT(c) 2019 STMicroelectronics
  *
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
  ******************************************************************************
  */
/* USER CODE END Header */

/* Define to prevent recursive inclusion -------------------------------------*/
#ifndef __MAIN_H
#define __MAIN_H

#ifdef __cplusplus
extern "C" {
#endif

#include <stdint.h>

/* Includes ------------------------------------------------------------------*/
#include "stm32f4xx_hal.h"
#include "stm32f4xx_hal_msp.h"
#include "arm_math.h"
#include "math.h"


TIM_HandleTypeDef htim3; // encoder


/* Private includes ----------------------------------------------------------*/
/* USER CODE BEGIN Includes */
#include "BSP_UART.h"
#include "BSP_GLCD.h"
#include "BSP_ADC.h"
#include "BSP_DAC.h"
#include "BSP_UIIO.h"

float g_graphBuffer1_V[ADC_INPUT_BUFFER_SIZE / 2];	// TODO: reduce number of redundant ADC buffers
float g_graphBuffer2_V[ADC_INPUT_BUFFER_SIZE / 2];	// TODO: reduce number of redundant ADC buffers


/* USER CODE END Includes */

/* Exported types ------------------------------------------------------------*/
/* USER CODE BEGIN ET */

/* USER CODE END ET */

/* Exported constants --------------------------------------------------------*/
/* USER CODE BEGIN EC */

/* USER CODE END EC */

/* Exported macro ------------------------------------------------------------*/
/* USER CODE BEGIN EM */

/* USER CODE END EM */

void HAL_TIM_MspPostInit(TIM_HandleTypeDef *htim);

/* Exported functions prototypes ---------------------------------------------*/
void Error_Handler(void);

/* USER CODE BEGIN EFP */

/* USER CODE END EFP */

/* Private defines -----------------------------------------------------------*/
#define BTN_USER_Pin GPIO_PIN_13
#define BTN_USER_GPIO_Port GPIOC

#define SWO_Pin GPIO_PIN_3
#define SWO_GPIO_Port GPIOB

#define TMS_Pin GPIO_PIN_13
#define TMS_GPIO_Port GPIOA
#define TCK_Pin GPIO_PIN_14
#define TCK_GPIO_Port GPIOA

/* USER CODE BEGIN Private defines */

/* USER CODE END Private defines */

#ifdef __cplusplus
}
#endif

#endif /* __MAIN_H */

/************************ (C) COPYRIGHT STMicroelectronics *****END OF FILE****/

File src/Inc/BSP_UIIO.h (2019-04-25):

#ifndef __BSP_UIIO_H
#define __BSP_UIIO_H


#include "main.h"
#include <stdint.h>




#define IN2_AC_Pin GPIO_PIN_8
#define IN2_AC_GPIO_Port GPIOA
#define IN1_AC_Pin GPIO_PIN_9
#define IN1_AC_GPIO_Port GPIOA
#define IN1_AA_Pin GPIO_PIN_10
#define IN1_AA_GPIO_Port GPIOA
#define IN2_AA_Pin GPIO_PIN_11
#define IN2_AA_GPIO_Port GPIOA

#define BTN_MAIN_Pin GPIO_PIN_4
#define BTN_MAIN_GPIO_Port GPIOB
#define BTN_1_Pin GPIO_PIN_5
#define BTN_1_GPIO_Port GPIOB
#define BTN_2_Pin GPIO_PIN_6
#define BTN_2_GPIO_Port GPIOB
#define BTN_3_Pin GPIO_PIN_7
#define BTN_3_GPIO_Port GPIOB
#define BTN_4_Pin GPIO_PIN_8
#define BTN_4_GPIO_Port GPIOB

#define LED_R_Pin GPIO_PIN_9
#define LED_R_GPIO_Port GPIOB

#define LED_G_Pin GPIO_PIN_10
#define LED_G_GPIO_Port GPIOB

#define ROT_ENC_A_Pin GPIO_PIN_6
#define ROT_ENC_A_GPIO_Port GPIOA
#define ROT_ENC_B_Pin GPIO_PIN_7
#define ROT_ENC_B_GPIO_Port GPIOA

struct UIIO_BtnTypedef;
typedef void (*UIIO_CallbackTypedef)(struct UIIO_BtnTypedef* caller);
typedef void (*UIIO_ScrollEventCallbackTypedef)(int16_t delta);

#define UIIO_BTN_STATE_LONG_PRESSED	0x02
#define UIIO_BTN_STATE_PRESSED		0x01
#define UIIO_BTN_STATE_RELEASED		0x00

#define UIIO_DEBOUNCE_TIME_MS		50
#define UIIO_LONG_PRESS_TIME_MS		500

#define UIIO_BTN_MAIN	0
#define UIIO_BTN_1		1
#define UIIO_BTN_2		2
#define UIIO_BTN_3		3
#define UIIO_BTN_4		4

typedef struct UIIO_BtnTypedef {
	uint16_t pin;
	GPIO_TypeDef* port;
	uint32_t pressTime;
	uint32_t releaseTime;
	uint8_t state;
	UIIO_CallbackTypedef onPress;		// called once on button press
	UIIO_CallbackTypedef onRelease;		// called once on button release
	UIIO_CallbackTypedef onLongPress;	// called once after 1000ms passes while button is pressed
	UIIO_CallbackTypedef onClick;		// called once if release occurs less than 1000ms after press
} UIIO_BtnTypedef;

int16_t UIIO_lastScrollCounter;
UIIO_ScrollEventCallbackTypedef UIIO_onScrollEvent;


// API functions
void UIIO_init();
void UIIO_update();
UIIO_BtnTypedef* UIIO_getButton(uint32_t id);

#endif

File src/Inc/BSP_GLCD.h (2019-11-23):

#ifndef __BSP_GLCD_H
#define __BSP_GLCD_H


#include "main.h"
#include "MonoGFX.h"
#include <stdint.h>


#define GLCD_DI_COMMAND	0
#define GLCD_DI_DATA	1

#define GLCD_CS_1	1
#define GLCD_CS_2	2
#define GLCD_CS_12	(GLCD_CS_1 | GLCD_CS_2)

#define GLCD_REG_DISPLAY_STATE		0x3E
#define GLCD_REG_START_LINE			0xC0
#define GLCD_REG_COLUMN_ADDR		0x40
#define GLCD_REG_PAGE_ADDR			0xB8

#define GLCD_DISPLAY_STATE_ON		0x01
#define GLCD_DISPLAY_STATE_OFF		0x01

#define GLCD_START_LINE_MASK		0x3F
#define GLCD_COLUMN_ADDR_MASK		0x3F
#define GLCD_PAGE_ADDR_MASK			0x07

#define GLCD_DATA_Port	GPIOC
#define GLCD_DB0_Pin	GPIO_PIN_0
#define GLCD_DB1_Pin	GPIO_PIN_1
#define GLCD_DB2_Pin	GPIO_PIN_2
#define GLCD_DB3_Pin	GPIO_PIN_3
#define GLCD_DB4_Pin	GPIO_PIN_4
#define GLCD_DB5_Pin	GPIO_PIN_5
#define GLCD_DB6_Pin	GPIO_PIN_6
#define GLCD_DB7_Pin	GPIO_PIN_7

#define GLCD_DI_Pin		GPIO_PIN_13
#define GLCD_DI_Port	GPIOB
#define GLCD_RW_Pin		GPIO_PIN_14
#define GLCD_RW_Port	GPIOB
#define GLCD_E_Pin		GPIO_PIN_9
#define GLCD_E_Port		GPIOC
#define GLCD_EN_Pin		GPIO_PIN_10
#define GLCD_EN_Port	GPIOC
#define GLCD_RST_Pin	GPIO_PIN_11
#define GLCD_RST_Port	GPIOC
#define GLCD_CS1_Pin	GPIO_PIN_12
#define GLCD_CS1_Port	GPIOC
#define GLCD_CS2_Pin	GPIO_PIN_15
#define GLCD_CS2_Port	GPIOB

#define GLCD_BACKLIGHT_Pin			GPIO_PIN_8
#define GLCD_BACKLIGHT_Port			GPIOC

TIM_HandleTypeDef htim4; // Signal timing
TIM_HandleTypeDef htim8; // PWM

MonoGFX_DisplayTypedef MonoGFXDisplay;

void HAL_TIM_PWM_MspInit(TIM_HandleTypeDef* htim_pwm);
void HAL_TIM_PWM_MspDeInit(TIM_HandleTypeDef* htim_pwm);
void MX_TIM4_Init(void);
void MX_TIM8_Init(void);

void MX_GLCD_GPIO_Init(void);

// API functions
void GLCD_init(uint32_t w, uint32_t h);
void GLCD_update();


void GLCDEN(int newState);
void GLCD_Write(int8_t cs_s, int8_t d_i, int8_t g_data);
void GLCD_Write_Block(int8_t m_data, int8_t cX, int8_t cY);
/*
void GLCD_Write_Char(char cPlace,char cX,char cY);
void GLCD_WriteString(const char* string,char X, char Y);
*/
void GLCD_setBacklight(float d);


#endif

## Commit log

2019-04-28 Fix bug where DAC output set to 3.3V generates 0V output
2019-05-05 Add auto connect feature on device added
2019-05-05 Minor changes
    [Nucleo.SchDoc]
2019-05-31 Fix "DAC output can't be connected to ADC input before current limiting resistor, for bode measurement (best case would be hardware support)." Fix "GLCD backlight and relay driver FET gates are not p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
    [GLCD.SchDoc, IO.SchDoc, InputStage.SchDoc, Nucleo.SchDoc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]
2019-06-10 Update gerbers, silk screen, hallglib outjob for JLCPCB
    [Oscilloscope.GBL, Oscilloscope.GBO, Oscilloscope.GBS, Oscilloscope.GTL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]
2019-06-17 Update readme and component designators.
    [InputStage.SchDoc, Oscilloscope.PrjPcb, OutputStage.SchDoc, hallglib.SchLib]
2019-11-23 Update MonoGFX and MonoGUI
    [Oscilloscope.PcbDoc]
